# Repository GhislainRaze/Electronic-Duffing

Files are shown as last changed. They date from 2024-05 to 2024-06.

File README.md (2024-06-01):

# An electronic Duffing oscillator

## Overview
This repository contains files for the realization of an electronic Duffing oscillator, i.e., a circuit whose behavior is governed Duffing's equation

$\qquad m\ddot{x}(t) + c\dot{x}(t) + kx(t) + k_3 x^3(t) = f_{ext}(t),$
    
with $m>0$, $c\geq0$ and $k_3\geq0$.

The circuit takes a signal proportional to $f_{ext}$ as input and outputs signals proportional to $x$ and $\dot{x}$. It allows for tunable values of the parameters $c$, $k$ and $k_3$ via the use of potentiometers. It is also possible to chose positive or negative values for $k$ and obtain a single- or double-well oscillator, respectively.

The circuit requires an external power source with symmetric supplies. The input and output signals can be imposed/measured with BNC connectors.

## References

The circuit diagrams were realized using KiCad7.0 (https://www.kicad.org/), inspired from the following works:

\[1\] B. K. Jones and G. Trefan, “The Duffing oscillator: A precise electronic analog chaos demonstrator for the undergraduate laboratory,” Am. J. Phys., vol. 69, no. 4, pp. 464–469, Apr. 2001, doi: [10.1119/1.1336838](https://doi.org/10.1119/1.1336838).

\[2\] K. Srinivasan, K. Thamilmaran, and A. Venkatesan, “Effect of nonsinusoidal periodic forces in Duffing oscillator: Numerical and analog simulation studies,” Chaos, Solitons & Fractals, vol. 40, no. 1, pp. 319–330, Apr. 2009, doi: [10.1016/j.chaos.2007.07.090](https://doi.org/10.1016/j.chaos.2007.07.090).

## More information

For more infomation, see the [documentation file](DOC/Electronic_Duffing.pdf).

## License

<p xmlns:cc="http://creativecommons.org/ns#" >This work is licensed under <a href="http://creativecommons.org/licenses/by/4.0/?ref=chooser-v1" target="_blank" rel="license noopener noreferrer" style="display:inline-block;">CC BY 4.0</a></p>

## Disclaimer

It is believed by the author that the design does not violate the Copyright of any other party. This cannot be guaranteed however, and the author accepts no liability for loss or damages that may be imposed upon the user by any Court of Law, statutory or other body, should it transpire that a similar circuit has been simultaneously or previously designed, published or patented by another party.

The author cannot be held responsible for any issues or damages either to life or property, or as monetary or physical losses, that might occur during the use of this circuit, either due to negligence, ignorance or lack of proper knowledge about the subject. It is entirely the user’s responsibility to determine the suitability of this design for the intended purpose, and to take enough precautions before assembling and using the circuit.

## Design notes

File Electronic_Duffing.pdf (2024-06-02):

## An electronic Duffing oscillator

Ghislain Raze

June 2024 - Rev 1.0

## 1 General schematics of the electronic Duffing oscillator

Figure 1 presents the (simplified) schematics of the electronic circuit used to implement a Duffing oscillator in [1], which is a slightly modified version of the circuit presented in [2, 3]. As shall be shown in Section 2, the relation between the input and output voltages, Vin and Vout, respectively, is a Duffing equation. An additional output V1 is proportional to the time derivative of Vout. The circuit contains three operational amplifiers that make up two integrators and an inverting amplifier, three buffers, and two analog multipliers. Three potentiometers (p1 - p3) are used to tune the parameters of the circuit.

The practical realization in [1] also uses four additional switches and three additional buffers. The latter are needed to ensure low-impedance output and high-impedance input signals. As for the switches, three of them are used to enable the measurement of the division ratios of the potentiometers, and the fourth one can be used to obtain either a single- or double-well oscillator. The circuit requires an external power source with symmetric supplies. The input and output signals can be

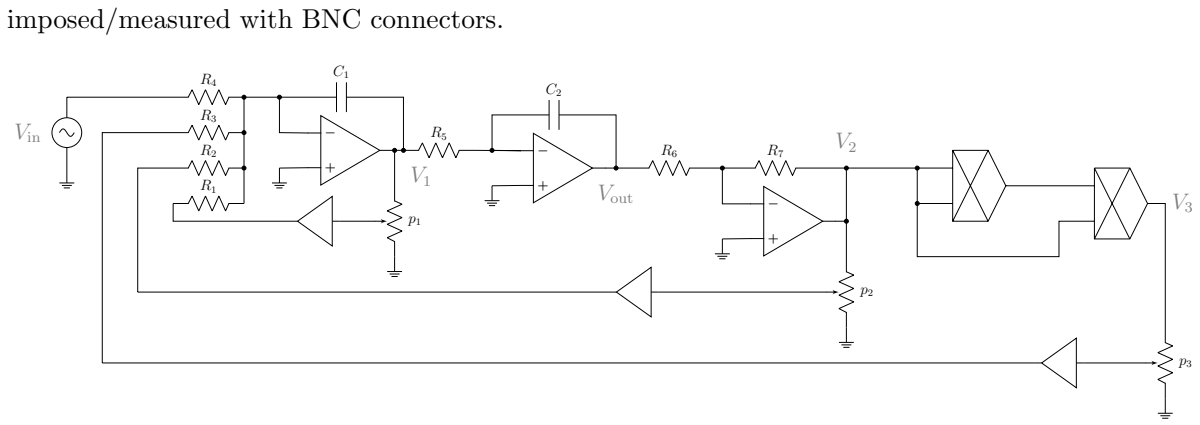
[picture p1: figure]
imposed/measured with BNC connectors.; Vout; Vin

Figure 1: Schematics of the electronic Duffing oscillator.

## 2 Governing equations

The following section assumes ideal operational amplifier behavior, i.e., no current flows into the input pins, and the voltage of these input pins is identical (due to the feedback action of the amplifier) [4]. It is also assumed that the buffers are perfect. Their output voltage is thus, from left to right, piVi (0 ≤ pi ≤ 1) for i = 1, 2, 3, where p1, p2 and p3 are the division ratios of the potentiometers.

Since the inverting input of the leftmost operational amplifier is (virtually) grounded, the currents going into R1 to R4 all go into C1, summing up to I1. This realizes a summing integrator governed by
V˙
1 = −

1
C1

I1 = −

1
C1
p1V1
R1

+

p2V2
R2

+

p3V3
R3

+

Vin
R4
. | (1)

The inverting input of the middle operational amplifier is also (virtually) grounded, and since the current going into R5 also goes into C2, this circuit implements an integrator governed by

V˙
out = −

V1

C2R5

. | (2)

Finally, since the inverting input of the rightmost amplifier is (virtually) grounded and the current going through R6 also goes into R7, the circuit implements an inverting amplifier, i.e.,

V2 = −

R7Vout
R6

(3)

The output of the first multiplier is gmV

2/2, and that of the third is

V3 = g

2
mV
3/2, | (4)

where gm is the gain of the electronic multiplier. Assembling Equations (1)-(4), one obtains a second-order differential equation for Vout:

C1C2R4R5V¨
out + p1

C2R4R5
R1

V˙
out + p2

R4R7
R2R6

Vout + p3

g

2

mR4R³
7
R3R³
6

V

3
out = Vin, | (5)

which is a Duffing equation.

Forcing signal

Velocity signal

Damping knob

Damping switch

Test points

Displacement signal

Power supply

Frequency knob

Nonlinearity switch

Nonlinearity knob

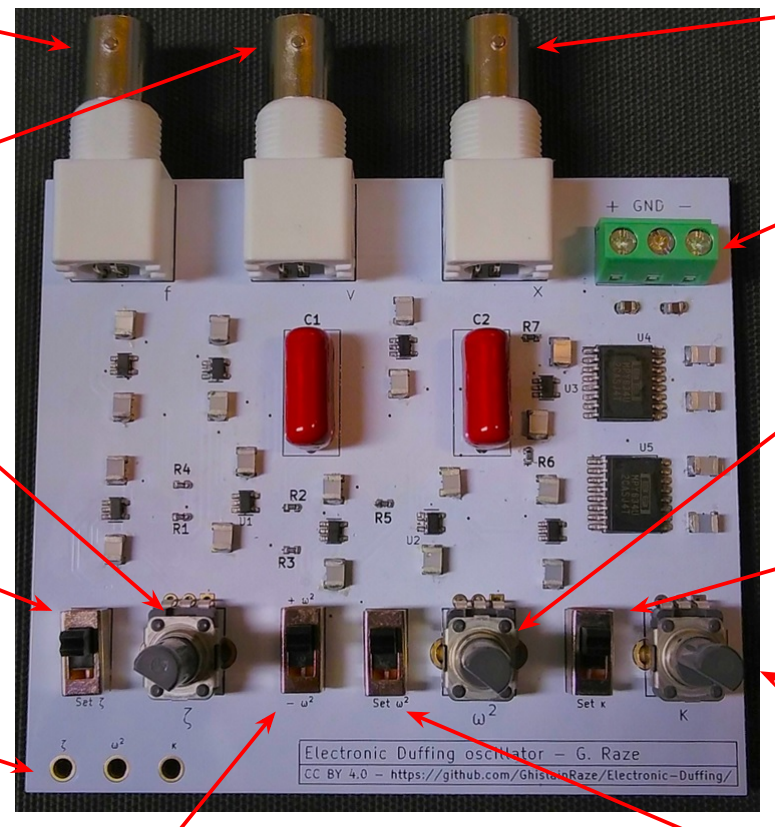
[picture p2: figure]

Single/double-well switch | Frequency switch

Figure 2: Picture of the electronic Duffing oscillator.

Figure 2 shows a photograph of the realization of the circuit in Figure 1 using Texas Instrument OPA210 operational amplifiers [5] and MPY634 multipliers [6].

## 3 Design choices

The electronic Duffing oscillator was designed to be interfaced with a MicroLabBox from dSPACE, hence had to be able to work with voltages in the ±10 V range. It was also desired to implement a weakly dissipative oscillator with very strong nonlinearity and relatively small resonance frequencies. These requirements guided the choice of the electrical parameters and integrated circuits, as briefly discussed in this section.

### 3.1 Electrical parameters

The rationale behind the choice of the electrical parameters of the circuit is now explained. Calculations were made based on the phase resonance backbone of the oscillator, which approximates the locus of maximum frequency response (for a weakly dissipative oscillator) [7].

Starting from Duffing’s equation,

mx¨(t) + cx˙(t) + kx(t) + k3x

3
(t) = f cos(ωt); | (6)

it is assumed that the oscillator is at phase resonance and its response can be approximated by a one-harmonic Fourier series
x(t) = a sin(ωt). | (7)

Using the harmonic balance method, i.e., inserting this ansatz into Equation (6) and balancing fundamental sine and cosine coefficients, one obtains the two equations
(
−mω²a + ka +

3k3
4

a

3 = 0

cωa = f

(8)

Inserting the second equation into the first one,

mω² − k −

3k3
4

f

2

c

2ω²

= 0, | (9)

from which the phase resonance backbone expression can be deduced as

ω =

### vuuut

k +

r
k

2 +

3mk3f

2

c

2
2m
. | (10)

This frequency can also be normalized with the natural frequency of the underlying linear oscillator (ω

2
0 = k/m)

ω
ω0

=

### vuuut

1 + r
1 +

3mk3f

2

k

2c

2
2
, | (11)

and the amplitude of the phase resonance backbone can be found with the second relation in Equation (8)

a =

f
cω
. | (12)

Equation (6) has four parameters, namely m, c, k and k3, that can be imposed to determine constraints that must be satisfied by the electrical parameters featured in Equation (5) (with x ≡ Vout and f ≡ Vin). Alternatively, more meaningful parameters, such as the linear natural frequency ω0 =

p
|k|/m, the damping ratio ζ0 = 2c/(mω0), as well as the frequency ratio ωmax/ω0 and the forcing level f when the oscillator undergoes maximum-amplitude oscillations (a = amax) can be imposed.

Considerations should be given to saturation of the integrated circuits when the oscillator is in its extreme regimes. Since Vout ≈ a, the second operational amplifier should only saturate close to the most extreme regime (a = amax). To guarantee that the third operational amplifier (V2) does not saturate before the second one, one can choose R6 = R7 (hence the amplitude of the voltage signals Vout and V2 will be identical, as per Equation (3)). As for V3, since gm = 0.1, the multipliers will saturate only if V2 saturates. Finally, concerning V1, Equations (2) and (7) show that

|V1|max ≈ C2R5ωmaxamax, | (13)

which puts the constraint C2R5ωmax ≤ 1 to avoid saturation of the first operational amplifier.

There can thus be seven constraints on the nine free parameters (seven resistances and two capacitances) depending on the user requirements. The electrical parameters may be selected depending on the commercially available electrical elements. Extreme values (low or high) could create undesirable loading effects and should be avoided.

### 3.2 Integrated circuits choice

OPA210 are precision operational amplifiers with very low offset voltage (≤5 µV ), which was the main motivation for their selection, together with their supply voltage range (Vs = ±18 V ). In addition, they feature a large bandwidth for this application (GBW = 18 MHz) for a relatively low quiescent current [5]. For simplicity, buffers were realized with the same operational amplifiers in an input follower configuration.

The MPY634 analog multipliers were chosen for their availability, for their wide bandwidth (10 MHz) and for their adequate voltage range [6].

### 3.3 Other elements

Bipolar capacitors with high capacitances were needed to allow for relatively low resonance frequencies (in order to require reasonable resistances). Most dielectric materials with a high dielectric constant generally also feature high dissipation, which entails parasitic damping in the oscillator that can be complicated to model. Polypropylene (PP) film capacitors were thus selected for C1 and C2 due to their low dissipation, since their relatively large volume is not a problem in this application.

Lossy integrators can be used instead of the integrators implemented with the first and second operational amplifiers by placing a resistor with large resistance in parallel to C1 and/or C2. Since there was no saturation issue with the integrators, and since the offsets are quite small in the tested version of the circuit, this was not deemed necessary.

Following the application note, bypass capacitors of 0.1µF were used for all integrated circuits [5], and bulk capacitors of 10µF were used for the power supply.

### 3.4 Parameter values

The design considerations outlined herein led to the parameters gathered in Table 1. Note that the potentiometers allow for a flexible range of parameters c, k and k3, but if the extreme values of these ranges are not satisfactory, other resistances and/or capacitances should be selected.

Parameter | Value
R1 (kΩ) | 100
R2 (kΩ) | 10
R3 (kΩ) | 1
R4 (kΩ) | 100
R5 (kΩ) | 1
R6 (kΩ) | 10
R7 (kΩ) | 10
C1 (µF) | 1
C2 (µF) | 1
gm (V⁻¹
) 0.1

Table 1: Electrical parameters of the electronic Duffing oscillator.

## 4 Circuit implementation

### 4.1 Use of the circuit

The electrical Duffing oscillator can be used in an experimental setup. This section briefly describes how to use the printed circuit board (PCB) in [1]. The reader can refer to Figure 2 to identify the different elements on the PCB.

BNC connectors are used to drive the circuit via the forcing signal port (symbol f on the PCB for Vin) and to measure its output (symbols x and v on the PCB for Vout and for V1, respectively). The circuit requires an external DC power source with symmetric supplies connected to the terminal block in the top right corner of the PCB. The supply voltage can range from ±8 V to ±18 V to comply with the maximum ratings of the integrated circuits [5, 6].

The parameters m, c, k and k3 in Equation (6) can be computed by a simple comparison with Equation (5). The value of p1, p2 and p3 can be adjusted by turning the knobs of the potentiometers. The switches Set ζ, Set ω

2 and Set κ on the PCB need to be up when the circuit is in operation, but can be down to make the determination of the value of these parameters easy when the circuit is not in operation. When they are down, they connect the potentiometers p1, p2 and p3 (respectively) to the positive power supply. The output of the buffer connected to the potentiometer is also connected to a test point (vias) in the bottom left of the PCB (ζ, ω

2 and κ on the PCB, respectively). If the positive supply voltage is Vs and the switches are down, the voltage measured at these test points should be equal to piVs, allowing the user to deduce the value of pi

The last switch (±ω

2 on the PCB) is used to implement a single- or double-well oscillator, when the switch is up or down, respectively. In the latter case, p2 is connected to Vout instead of V2 (cf. Figure 1).

### 4.2 Non-ideal behavior

Although the circuit does replicate the dynamics of a Duffing oscillator quite faithfully, this replication is not perfect due to several non-idealities. The ones suspected to be the most impactful are listed hereafter:

1. Voltage offsets: there exists voltage offsets at the input and output of the different integrated circuits, preventing a perfect symmetry in the oscillator.
2. Imperfect integrators: due to its finite open-loop gain, an operational amplifier used in an integrator will not perform an exact integration [5]. As also mentioned earlier, dissipation in the capacitors may also be the cause for an imperfect integrator behavior.
3. Imperfect nonlinearity: analog multipliers can also feature a small error (the output will not exactly be the product of the input voltages) [6].

## 5 Validation

Table 1 gathers the electrical parameters of the electronic oscillator. The potentiometers were adjusted to have a small dissipation (p1 = 0.1311), relatively small resonance frequency (p2 = 0.1923) and maximized nonlinearity (p3 = 0.9887). From these values and those in Table 1, using Equation (5), it was possible to deduce the theoretical characteristics of the oscillator given in Table 2. They were compared to an identification with the nonlinear frequency subspace identification (FNSI) method [8] using data from a swept-up sine test between 50 and 200 rad/s with a forcing amplitude of 0.03 V.

Table 2: Theoretical and identified parameters of the electronic Duffing oscillator.

Parameter | Theoretical value | Identified value
m (s

2

) | 10⁻⁴ | 1.0461 × 10⁻⁴
c (s) | 1.3×10⁻⁴ | 1.4231×10⁻⁴
k (-) | 1.923 | 1.8099
k3 (V

−2
) | 0.9887 | 1.0077

Small differences can be observed between theoretical and experimental values. Part of it can be attributed to the uncertainty on the capacitances (±5%). There could also be non-idealities in the circuit that may come from non-ideal operational amplifiers and multipliers characteristics.

## References

[1] G. Raze, “An electronic Duffing oscillator,” 2024. [Online]. Available: https://github.com/GhislainRaze/Electronic-Duffing (https://github.com/GhislainRaze/Electronic-Duffing)
[2] B. K. Jones and G. Trefan, “The Duffing oscillator: A precise electronic analog chaos demonstrator for the undergraduate laboratory,” Am. J. Phys., vol. 69, no. 4, pp. 464–469, apr 2001. [Online]. Available: https://pubs.aip.org/aapt/ajp/article/69/4/464-469/1055595
[3] K. Srinivasan, K. Thamilmaran, and A. Venkatesan, “Effect of nonsinusoidal periodic
forces in Duffing oscillator: | Numerical and analog simulation studies,” Chaos, Solitons
& Fractals, | vol. 40, | no. 1, | pp. 319–330, | apr 2009. [Online]. Available: | https:
//linkinghub.elsevier.com/retrieve/pii/S0960077907005796
[4] P. Horowitz and W. Hill, The Art of Electronics, 3rd ed. Cambridge University Press, 2015.
[5] OPAx210 2.2-nV/√Hz Precision, Low-Power, 36-V Operational Amplifiers, Texas Instruments,

08 2021. [Online]. Available: https://www.ti.com/lit/ds/symlink/opa210.pdf

[6] Wide Bandwidth PRECISION ANALOG MULTIPLIER, Texas Instruments, 2004. [Online]. Available: https://www.ti.com/lit/ds/symlink/mpy634.pdf
[7] M. Cenedese and G. Haller, “How do conservative backbone curves perturb into forced responses? A Melnikov function analysis,” Proceedings of the Royal Society A: Mathematical, Physical and Engineering Sciences, vol. 476, no. 2234, p. 20190494, feb 2020. [Online]. Available: https://royalsocietypublishing.org/doi/10.1098/rspa.2019.0494
[8] J. No¨el and G. Kerschen, “Frequency-domain subspace identification for nonlinear mechanical systems,” Mechanical Systems and Signal Processing, vol. 40, no. 2, pp. 701–717, nov 2013. [Online]. Available: https://linkinghub.elsevier.com/retrieve/pii/S088832701300318X

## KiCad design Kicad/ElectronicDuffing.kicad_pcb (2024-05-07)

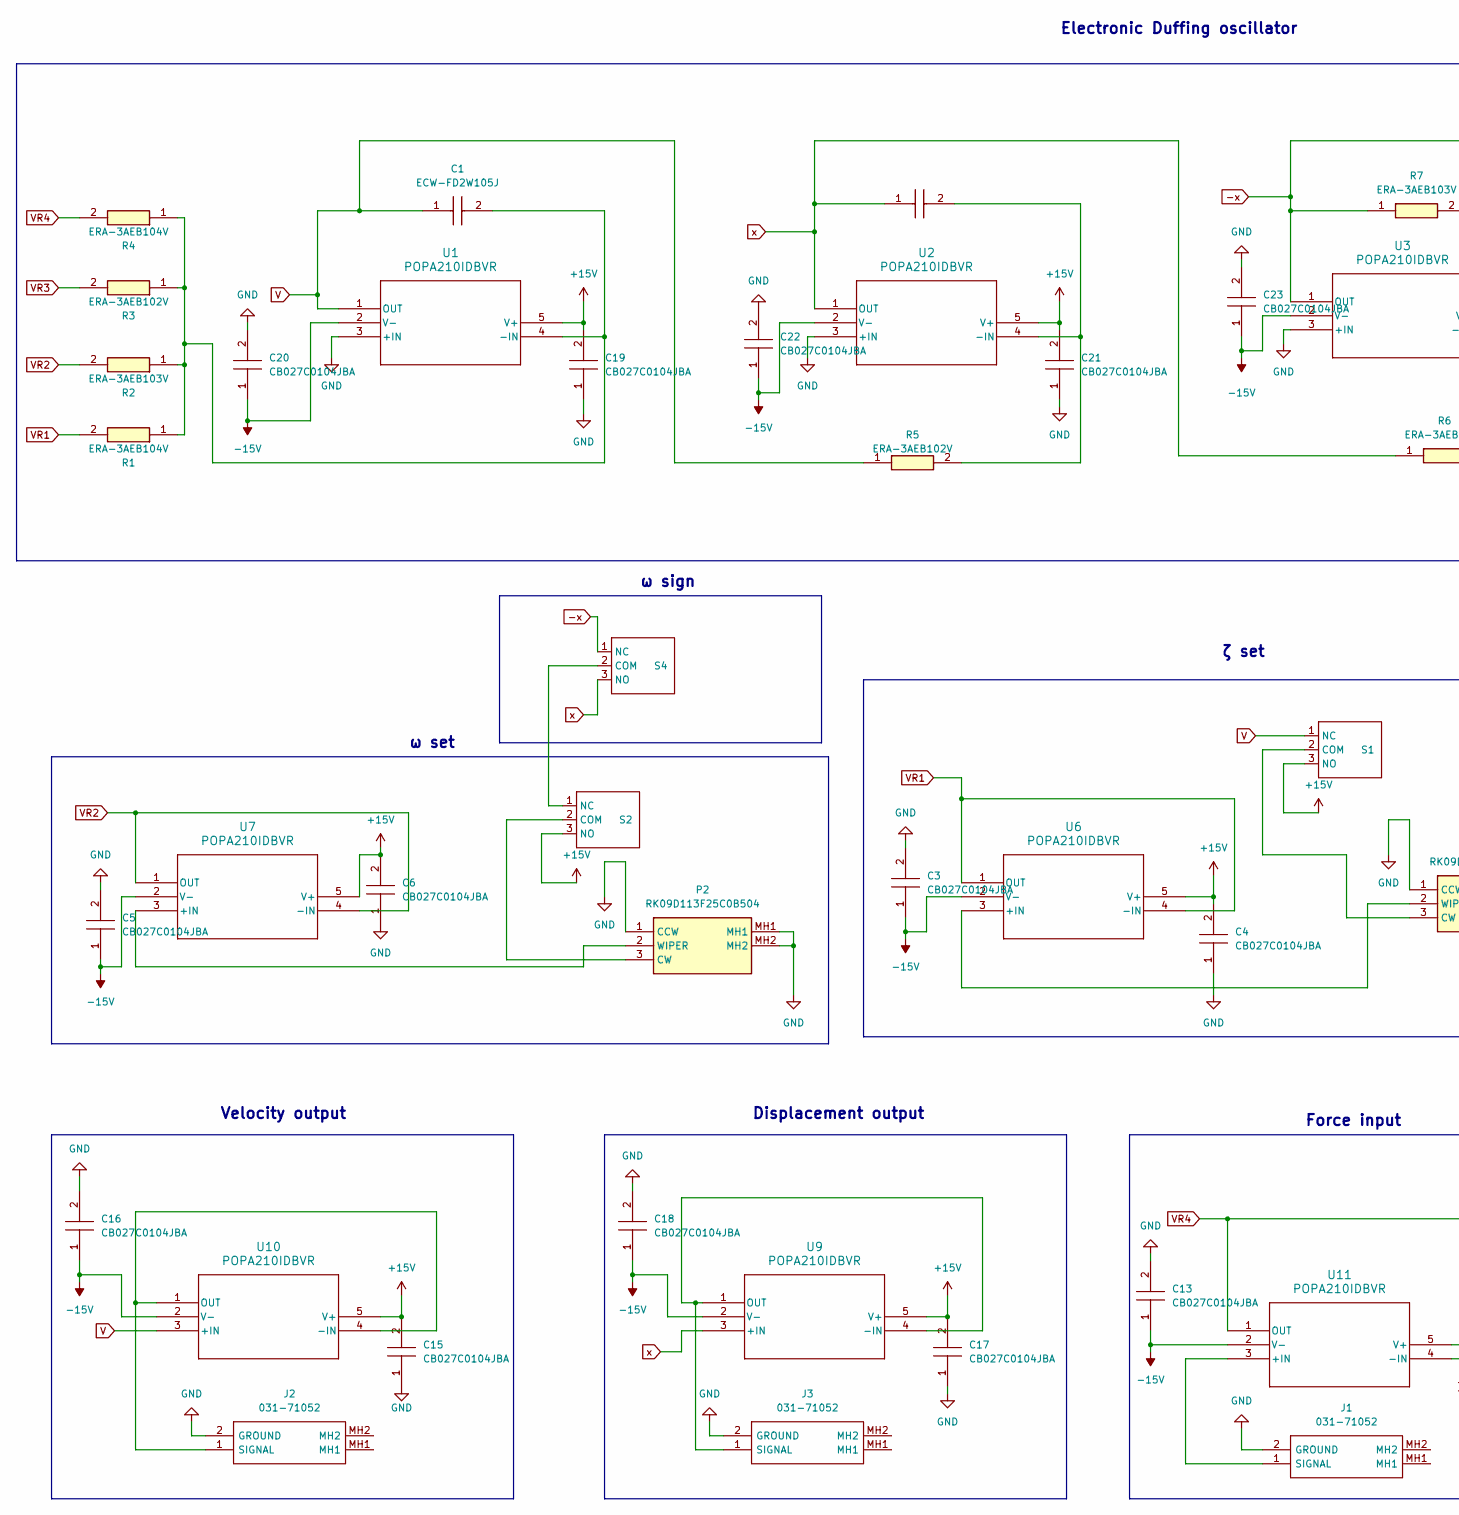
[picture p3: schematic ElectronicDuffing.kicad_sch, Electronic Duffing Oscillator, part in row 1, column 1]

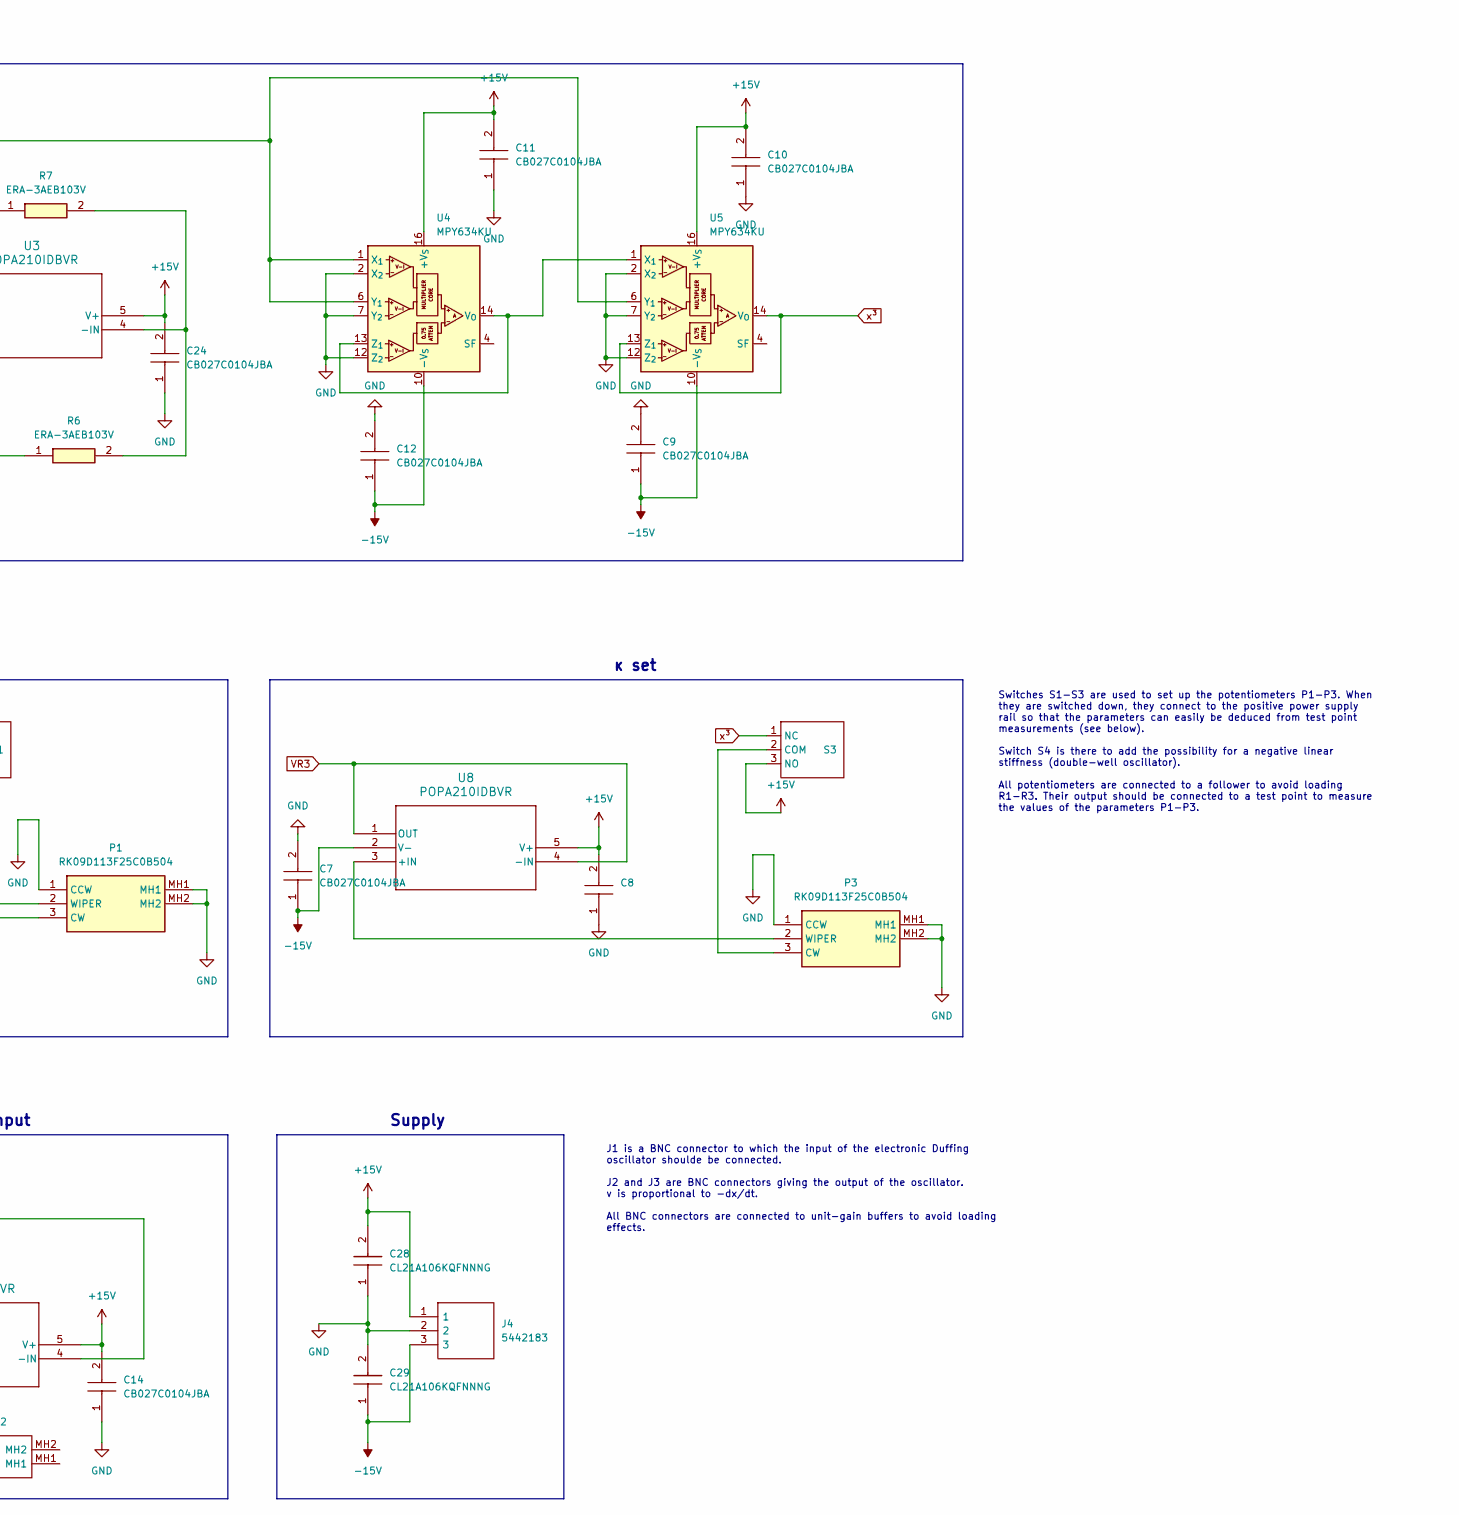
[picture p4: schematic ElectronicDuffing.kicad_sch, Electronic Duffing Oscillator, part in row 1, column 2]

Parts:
C1, C2: ECW-FD2W105J; ECWFD2W105J; Mouser Part Number 667-ECW-FD2W105J
C3, C4, C5, C6, C7, C8, C9, C10, C11, C12, C13, C14, C15, C16, C17, C18, C19, C20, C21, C22, C23, C24: CB027C0104JBA; CAPC3325X230N; Mouser Part Number 581-CB027C0104JBA
C28, C29: CL21A106KQFNNNG; CAPC2012X135N; Mouser Part Number 187-CL21A106KQFNNNG
J1, J2, J3: 031-71052; 03171052; Manufacturer_Part_Number 031-71052
J4: 5442183; Mouser Part Number 651-5442183
P1, P2, P3: RK09D113F25C0B504; Mouser Part Number 688-RK09D113F25-500K
R1, R4: ERA-3AEB104V; ERA3AEB101V; Mouser Part Number 667-ERA-3AEB104V
R2, R6, R7: ERA-3AEB103V; ERA3AEB101V; Mouser Part Number 667-ERA-3AEB103V
R3, R5: ERA-3AEB102V; ERA3AEB101V; Mouser Part Number 667-ERA-3AEB102V
S1, S2, S3, S4: MFP120
U1, U2, U3, U6, U7, U8, U9, U10, U11: POPA210IDBVR; SOT23_DBV_TEX
U4, U5: MPY634KU; SOIC-16W_7.5x10.3mm_P1.27mm

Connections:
+15V: C4.2, C6.2, C8.2, C10.2, C11.2, C14.2, C15.2, C17.2, C19.2, C21.2, C24.2, C28.2, J4.1, S1.3 (NO), S2.3 (NO), S3.3 (NO), U1.5 (V+), U2.5 (V+), U3.5 (V+), U4.16 (+V_{S}), U5.16 (+V_{S}), U6.5 (V+), U7.5 (V+), U8.5 (V+), U9.5 (V+), U10.5 (V+), U11.5 (V+)
-15V: C3.1, C5.1, C7.1, C9.1, C12.1, C13.1, C16.1, C18.1, C20.1, C22.1, C23.1, C29.1, J4.3, U1.2 (V-), U2.2 (V-), U3.2 (V-), U4.10 (-V_{S}), U5.10 (-V_{S}), U6.2 (V-), U7.2 (V-), U8.2 (V-), U9.2 (V-), U10.2 (V-), U11.2 (V-)
-x: R7.1, S4.1 (NC), U3.1 (OUT), U4.1 (X_{1}), U4.6 (Y_{1}), U5.6 (Y_{1})
GND: C3.2, C4.1, C5.2, C6.1, C7.2, C8.1, C9.2, C10.1, C11.1, C12.2, C13.2, C14.1, C15.1, C16.2, C17.1, C18.2, C19.1, C20.2, C21.1, C22.2, C23.2, C24.1, C28.1, C29.2, J1.2 (GROUND), J2.2 (GROUND), J3.2 (GROUND), J4.2, P1.1 (CCW), P1.MH1, P1.MH2, P2.1 (CCW), P2.MH1, P2.MH2, P3.1 (CCW), P3.MH1, P3.MH2, U1.3 (+IN), U2.3 (+IN), U3.3 (+IN), U4.2 (X_{2}), U4.7 (Y_{2}), U4.12 (Z_{2}), U5.2 (X_{2}), U5.7 (Y_{2}), U5.12 (Z_{2})
unnamed: J1.1 (SIGNAL), U11.3 (+IN)
unnamed: J2.1 (SIGNAL), U10.1 (OUT), U10.4 (-IN)
unnamed: J3.1 (SIGNAL), U9.1 (OUT), U9.4 (-IN)
unnamed: P1.3 (CW), S1.2 (COM)
unnamed: P1.2 (WIPER), U6.3 (+IN)
unnamed: P2.3 (CW), S2.2 (COM)
unnamed: P2.2 (WIPER), U7.3 (+IN)
unnamed: P3.3 (CW), S3.2 (COM)
unnamed: P3.2 (WIPER), U8.3 (+IN)
unnamed: S2.1 (NC), S4.2 (COM)
unnamed: C1.2, R1.1, R2.1, R3.1, R4.1, U1.4 (-IN)
unnamed: C2.2, R5.2, U2.4 (-IN)
unnamed: R6.2, R7.2, U3.4 (-IN)
unnamed: U4.13 (Z_{1}), U4.14 (V_{O}), U5.1 (X_{1})
V: C1.1, R5.1, S1.1 (NC), U1.1 (OUT), U10.3 (+IN)
VR1: R1.2, U6.1 (OUT), U6.4 (-IN)
VR2: R2.2, U7.1 (OUT), U7.4 (-IN)
VR3: R3.2, U8.1 (OUT), U8.4 (-IN)
VR4: R4.2, U11.1 (OUT), U11.4 (-IN)
x: C2.1, R6.1, S4.3 (NO), U2.1 (OUT), U9.3 (+IN)
x³: S3.1 (NC), U5.13 (Z_{1}), U5.14 (V_{O})

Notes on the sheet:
ω set
κ set
ω sign
Force input
J1 is a BNC connector to which the input of the electronic Duffing oscillator shoulde be connected. J2 and J3 are BNC connectors giving the output of the oscillator. v is proportional to -dx/dt. All BNC connectors are connected to unit-gain buffers to avoid loading effects.
Switches S1-S3 are used to set up the potentiometers P1-P3. When they are switched down, they connect to the positive power supply rail so that the parameters can easily be deduced from test point measurements (see below). Switch S4 is there to add the possibility for a negative linear stiffness (d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
ζ set
Supply
Displacement output
Velocity output
Electronic Duffing oscillator

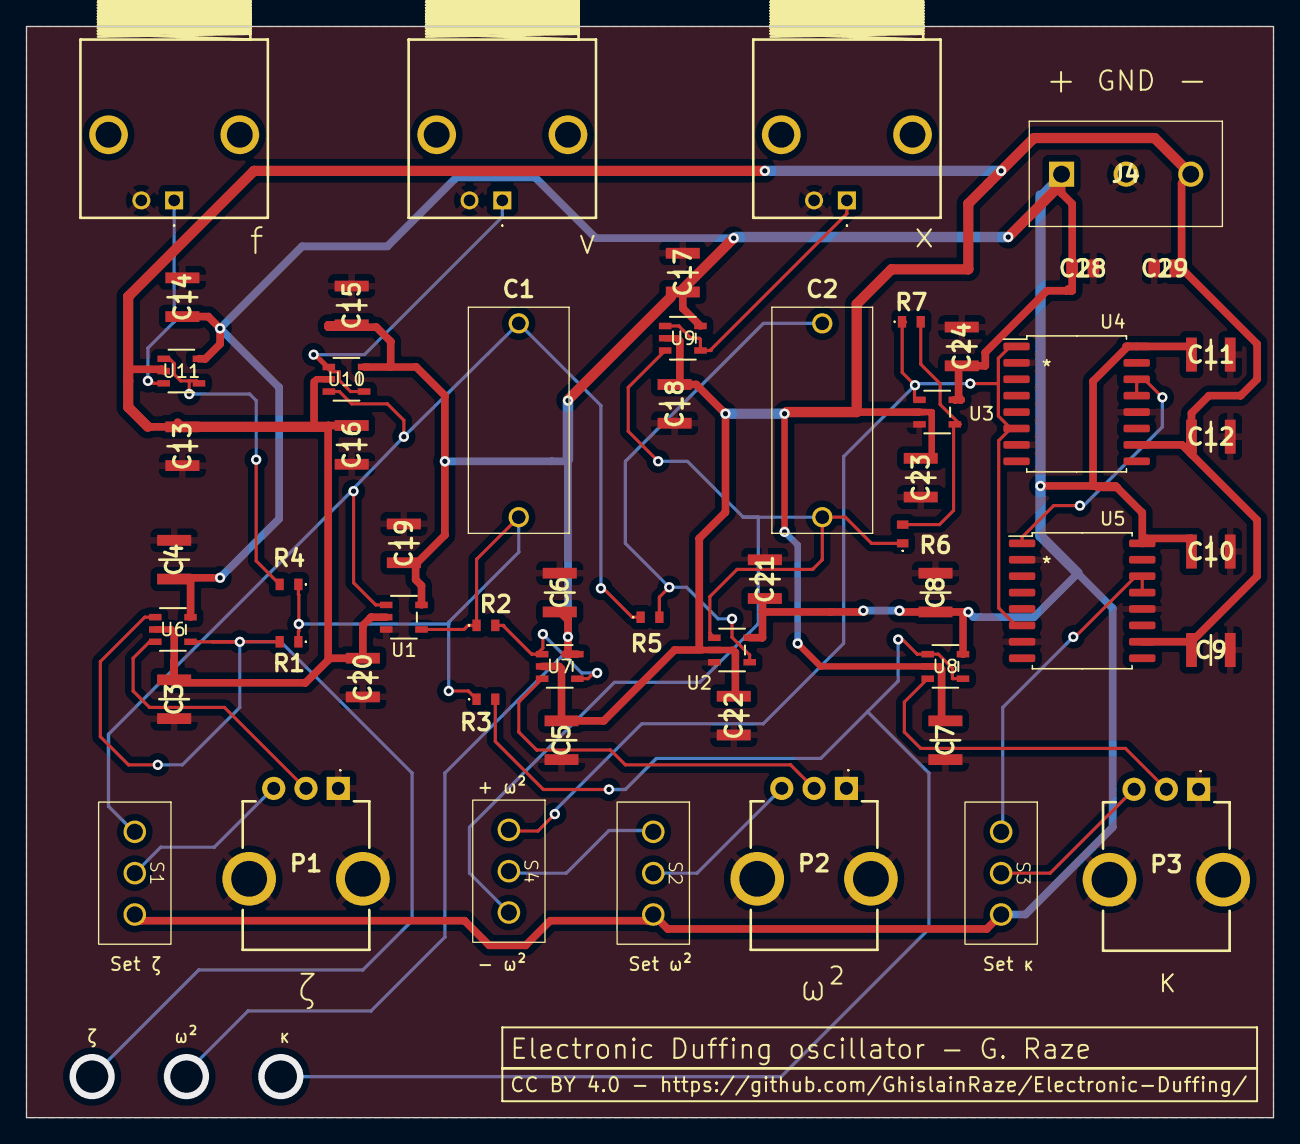
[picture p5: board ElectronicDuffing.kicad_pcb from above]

Board: 2 copper layers, 96.5 x 84.5 mm, 55 parts (0 on the bottom side), 25 nets.

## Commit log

2024-05-07 KiCad files upload
    [ElectronicDuffing.kicad_pcb, ElectronicDuffing.kicad_sch]
2024-05-07 Add Gerber files
    [ElectronicDuffing-B_Cu.gbr, ElectronicDuffing-B_Mask.gbr, ElectronicDuffing-B_Paste.gbr, ElectronicDuffing-B_Silkscreen.gbr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]

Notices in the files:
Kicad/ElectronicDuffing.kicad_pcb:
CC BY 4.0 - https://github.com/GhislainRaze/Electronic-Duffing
